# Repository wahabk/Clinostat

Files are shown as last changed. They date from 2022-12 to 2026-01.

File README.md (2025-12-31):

# OpenClino - Open-source 3D clinostat

Open-source 3D clinostat. A clinostat is a small scale [microgravity simulator](https://en.wikipedia.org/wiki/Random_positioning_machine).

Clinostat cad! cadModel
Clinostat real! realBuilt

This is based on the European Space Agency's work, specifically on [Jack Van Loon's clinorotation work](https://doi.org/10.3389/fpls.2019.01577).

OpenClino is designed to be simple, accessible, affordable, and **reliable**. It is designed to make use of 3D printing's strengths and requires *no machining* and minimum tools. To build OpenClino all non-printed parts are available off the shelf, mainly 3d printer stepper motors, belts, controllers, and skateboard bearings. All these parts are rated for thousands of hours of operation, and I have fully tested OpenClino to run for a minimum of 100 hours.

## Documentation

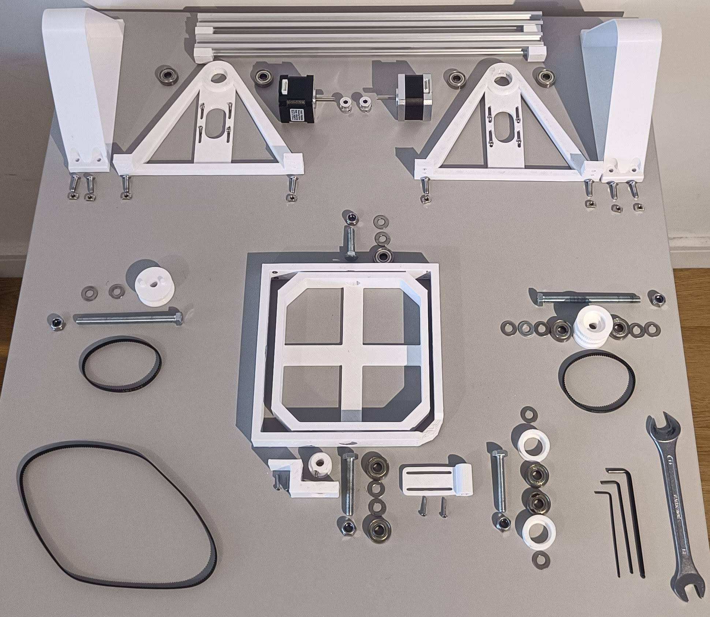
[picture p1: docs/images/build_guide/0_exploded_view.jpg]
Clinostat build!


I have provided:

- Docs in [`docs/1_documentation.md/`](docs/1_documentation.md) including circuit diagram.
- Code in [`src/`](src/openclino.ino)
- Code documentation in [`docs/4_code_documentation.md/`](docs/4_code_documentation.md/)
- 3D print files as .3MF in [`3d_files/`](3d_files/)
- Bill of materials in [`docs/2_BOM.md/`](docs/2_BOM.md/)
- Build guide in [`docs/3_build_guide.md/`](docs/3_build_guide.md/)

## Quick Usage

To run in clinorotation mode simply add these to your arduino's loop function, this will run the x axis at 3 rpm and the y axis at 4:

```cpp
void loop() {
    spin_continuous(3,4);
}
```

Don't forget to set the output pins for you motor controllers!

## Partial Gravity Simulation

Partial gravity simulations are now possible since Version 0.5.0. Instructions available in [`docs/1_documentation.md/`](docs/1_documentation.md).

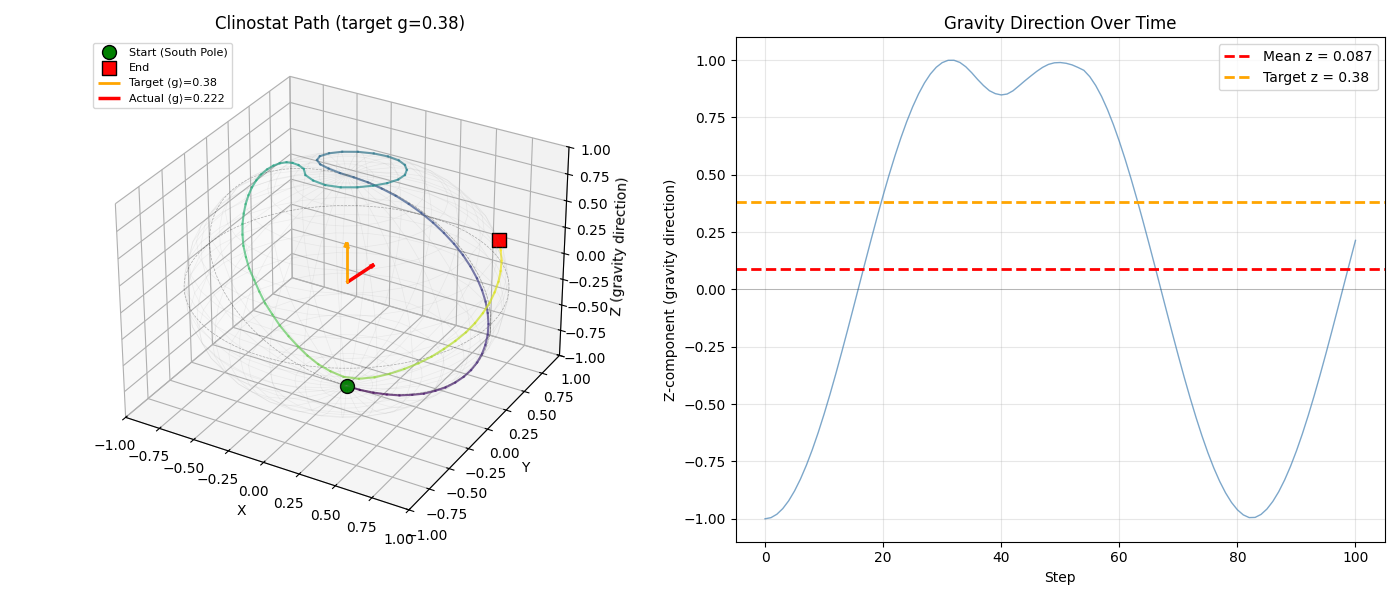
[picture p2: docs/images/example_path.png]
Partial gravity simulation.


## Contributors

[Dan Dragomirescu @dragomda](https://github.com/dragomda)

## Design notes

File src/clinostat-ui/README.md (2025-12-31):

# OpenClino UI

This directory contains scripts to run OpenClino with an LVGL screen connected to your Arduino.

Author: Dan Dragomirescu @dragomda

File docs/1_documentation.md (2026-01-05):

# OpenClino

It is very difficult to access a 3D clinostat, there are some companies that sell it but can be prohibitively expensive for gravity research. OpenClino can be built for £100 using off the shelf parts. OpenClino can run in continuous clinorotation or as a Random Positioning Machine (RPM).

> [!NOTE]  
> Since Version 0.3.0 remember to run the [calibration procedure](#usage--calibration).

## Definitions

- X body is the outer body. 
- Y body is the inner body.
- Motor pulleys attach to the motor.
- X/Y pulleys attach to the body.
- The "`m2y`" pulley is the one with 2 belts attached.
- The "`y_turn`" is the bearings bending the long y belt.
- The "`y_guide`" is the L shaped bracket holding the y pulley.

## Circuit design

This is a very simple arduino circuit with a button and 2 stepper motor controllers.

I base the circuit on [this great article by lastminuteengineers](https://lastminuteengineers.com/a4988-stepper-motor-driver-arduino-tutorial/]).

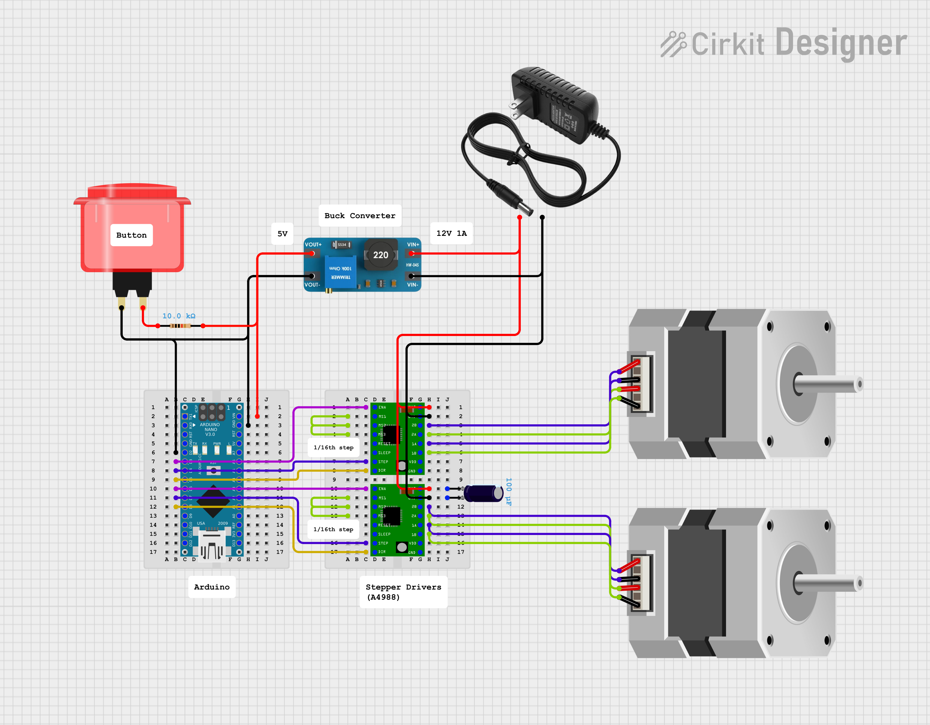
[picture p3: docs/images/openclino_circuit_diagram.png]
Clinostat circuit. Circuit diagram. Made with Cirkit Designer.


### Optional: MicroSD card reader

You can optionally add a MicroSD card reader to the circuit

Again I base the circuit on [this great article by lastminuteengineers](https://lastminuteengineers.com/arduino-micro-sd-card-module-tutorial/]).

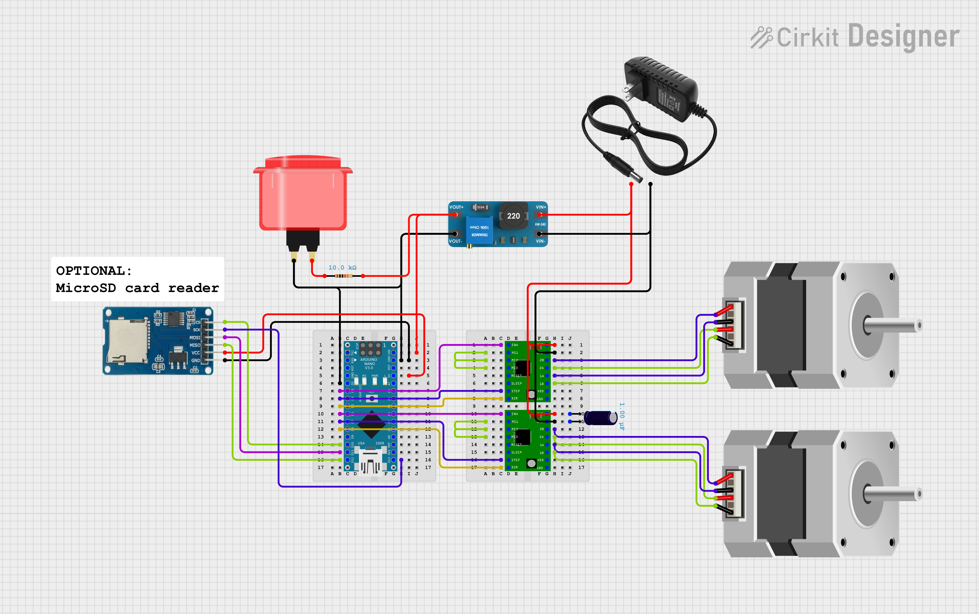
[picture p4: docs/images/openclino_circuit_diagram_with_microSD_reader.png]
Clinostat with MicroSD circuit. Circuit w/ SD diagram. Made with Cirkit Designer.


## Code

[OpenClino Documentation.](4_code_documentation.md)

## Usage
### Calibration

To calibrate the Y-axis correction factor, follow these steps:

1. Upload the code to your Arduino.
2. Open the Serial Monitor in the Arduino IDE.
3. Center the frames so that they are overlapping.
4. Press the button connected to the Arduino to start the calibration process.
5. The Y-axis motor will rotate by 360 degrees.
6. The Serial Monitor will prompt you to enter the actual degrees the Y-axis rotated.
7. Enter the measured degrees in the Serial Monitor and press Enter.
8. The new Y-axis correction factor will be calculated and displayed in the Serial Monitor.
9. Manually update the `yCorrection` variable in the code with the new correction factor.

Example:

```cpp
double yCorrection = 1.5; // Update this value with the new correction factor
```

> [!NOTE]  
> You might have to run the calibration a couple of times to get the right correction. The effect of the outer body on the inner body is dependant on friction in the system which is widely variable.

Now your clinostat is ready to use! To run in clinorotation mode simply add these to your arduino's loop function, this will run the x axis at 2 RPM and the y axis at 4:

```cpp
void loop() {
    spin_continuous(2,4);
}
```

### Partial gravity simulation

The scripts for partial gravity path generation can be found in `src/openclino/partial_gravity/`.

Partial gravity simulations require a more complex path to follow, which the arduino is not able to compute at runtime, therefore, this requires generating a path on your computer using a python script and reading the path on the arduino using a MicroSD card reader.

The method is based on a geodesic random walk on a spheroid. The sphere is sampled evenly which usually results in close to 0g, and the error from the target Gz is computed. A drift term is added to the clinostat's path to bias the running average Gz to converge to the target G. This is based on the paper - [Novel, Moon and Mars, partial gravity simulation paradigms and their effects on the balance between cell growth and cell proliferation during early plant development](https://www.ncbi.nlm.nih.gov/pmc/articles/PMC5884789/).

After setting up your arduino with a MicroSD card reader as shown in the Circuit Design documentation above, follow these steps:

1. Generate a path with `python generate_random_walk_path.py`
2. Visualise the path and average Gz with the above script until you are happy with the path. You may need to adjust `n_steps`, `step_size`, and the `control_window`.
3. Copy the generated `path.txt` to a MicroSD card and insert into the arduino reader.
4. Run `openclino.ino` with `follow_path();` uncommented. The serial Monitor will help debug any issues with the SD card.

### SD Card debugging

There can be faults with the MicroSD card reader, the card itself, or the file added.

1. Make sure the file is called `path.txt` or `PATH_FILENAME` is adjusted in `openclino.cpp`.
2. Make sure the file is in the root directory of the SD card (not inside another folder).
3. Use the debugging scripts to test the SD card and path file separately. Open your Serial Monitor and follow the instructions:
   1. Ensure the SD card and reader work with `test_sd/test_sd.ino`. This will read the SD card, write some text to the file `test.txt` and then read the file.
   2. Test that the path file works with `test_path/test_path.ino`. This will read each file line by line and verify it's format.

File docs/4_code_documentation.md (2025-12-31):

# OpenClino Documentation

This document provides reference information about the functions used to control stepper motors in the Arduino project. Each function is described with its purpose, parameters, and behavior. The documentation is generated using AI.

## Functions

### `void enable(bool enableX, bool enableY)`

Enables or disables the X and Y motors.

- **Parameters:**
  - `enableX` (bool): If `true`, enables the X-axis motor; if `false`, disables it.
  - `enableY` (bool): If `true`, enables the Y-axis motor; if `false`, disables it.

---

### `void spin_degs(float Q1_target, float Q2_target, float maxRPM = 10, int finalDelay = 100)`

Spins the X and Y motors by specified degrees at specified speeds.

- **Parameters:**
  - `Q1_target` (float): Degrees to rotate the X-axis motor.
  - `Q2_target` (float): Degrees to rotate the Y-axis motor.
  - `maxRPM` (float, default = 10): Maximum speed of the motors in RPM.
  - `finalDelay` (int, default = 100): Delay in milliseconds after stopping the motors.

---

### `void spin_continuous(float speedX = 10, float speedY = 10, int buttonDelay = 1000)`

Spins the X and Y motors continuously at specified speeds until a button is pressed.

- **Parameters:**
  - `speedX` (float, default = 10): Speed of the X-axis motor in RPM.
  - `speedY` (float, default = 10): Speed of the Y-axis motor in RPM.
  - `buttonDelay` (int, default = 1000): Delay in milliseconds after stopping the motors.

---

### `void calibrate_y_correction()`

Calibrates the Y-axis correction factor by rotating the Y-axis motor and measuring the actual rotation.

---

## Tests

### `void test_pulley_ratios()`

Tests the pulley ratios by rotating the X and Y motors by 360 degrees and back.

---

### `void test_spin_degs_multi()`

Tests the `spin_degs` function with multiple rotations.

---

### `void follow_path()`

Reads `PATH_FILENAME` (by default `path.txt`) from an SD card, and executes `spin_degs()` on each line of the file. The function will error if the SD card can't be read or if the file is not found.

---

### `void setup()`

Initializes the Arduino pins and serial communication, and prints a welcome message.

---

### `void loop()`

Main loop that reads the button state and performs actions based on the button press.

- **Behavior:**
  - Turns off motors when the button is not pressed.
  - When the button is pressed, it turns on the motors, lights up the built-in LED, and runs calibration and test functions.

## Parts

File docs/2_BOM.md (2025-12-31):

# Bill of Materials

#### To Buy

| Category     | Quantity | Description                                 | Specifications              |
|--------------|----------|---------------------------------------------|-----------------------------|
| Electronics  | 1        | Arduino (your choice)                       | -                           |
|              | 2        | Nema 17 motors                              | 0.42Nm                      |
|              | 2        | Stepper motor controllers                   | A4988 drivers are cheap. TMC2208 drivers will give better, silent operation with less vibration.                       |
|              | 1        | Power supply                                | -                           |
|              | 1        | MicroSD card reader                         | Optional, required for partial gravity. 5V 6 spin SPI interface SD card reader |
| Hardware     | 2        | GT2 belts                                   | 200mm, 6mm width            |
|              | 1        | GT2 belt                                    | 500mm, 6mm width            |
|              | 2        | Stepper motor timing pulleys                | 16 tooth                    |
|              | 1        | GT-2 Pulley (y_pulley)                      | 30 tooth, 8mm bore, 6mm width |
|              | 1        | Aluminium extrusion                         | 1mx20mmx20mm (cut in half)  |
|              | 12       | Skateboard bearings                         | 8mm (ID), 22mm (OD)         |
| Bolts        | 4        | Hex bolts                                   | M8 by 60mm                  |
|              | 2        | Hex bolts                                   | M8 by 100mm                 |
|              | 8        | Alan bolts                                  | M3 by 12mm                  |
|              | 12       | Alan bolts                                  | M5 by 16mm                  |
|              | 13       | Washers                                     | M8 (8mm ID, 16mm OD)        |
| Miscellaneous| 1        | Printing filament                           | 1KG, your choice of filament|

#### To Print

| Quantity | Description    | Note              |
|----------|----------------|-------------------|
| 2        | m_enclosure    | -                 |
| 2        | m_mounts       | -                 |
| 1        | x_body         | -                 |
| 1        | x_pulley       | -                 |
| 1        | y_body         | -                 |
| 1        | m2y_pulley     | Needs Supports    |
| 1        | y_turn         | -                 |
| 2        | y_turn_pulley  | -                 |
| 1        | y_guide        | -                 |

All files are available in `3d_files/`.

All the parts are printed with 20% infill, and I use an Ender 3 printer. I usually have to sand down the edges due to stringing etc.
According to your printer's over/under extrusion you might have to sand down edges, or add silicon tape to the bolt heads so they key into the bodies.
I personally prefer to use a brim.

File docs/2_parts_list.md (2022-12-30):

# Parts list

## To buy

- 2 x nema 17 motors
- 2 x stepper motor controllers (A4988)
- 2 x 180mm GT2 belts
- 1 x 220mm GT2 belt
- 2 x stepper motor pulleys
- 1m 20x20 aluminium extrusion
- 12 x 8mm skateboard bearings

Hardware
- 4 x m8 by 60mm hex bolts
- 2 x m8 by 100mm hex bolts
- 8 x m3 bolts
- 12 x m5 by 

- 1KG of your printing filament of choice

## To print

- 2 x m_enclosure
- 2 x m_mounts
- x_body
- x_pulley
- y_body
- m2y_pulley
- y_turn
- 2 x y_turn_pulley
- y_guide
- y_pulley

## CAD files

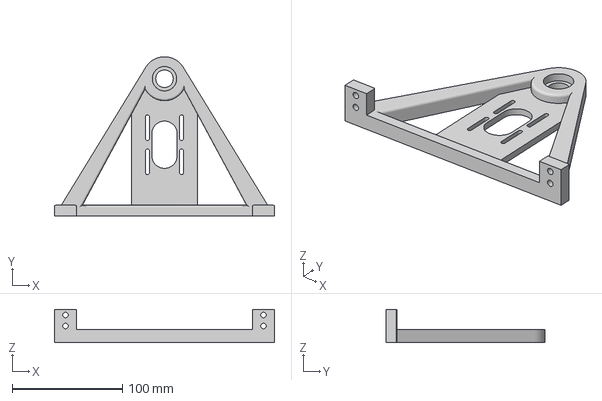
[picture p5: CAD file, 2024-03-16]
3d_files/m_base v9.3mf
200.0 x 145.0 x 30.0 mm

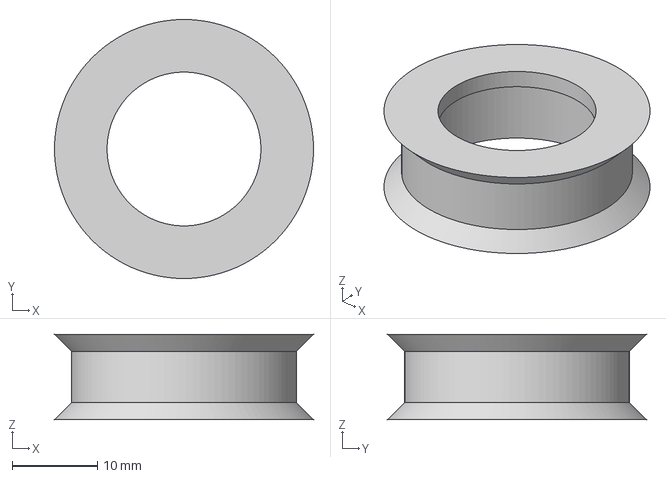
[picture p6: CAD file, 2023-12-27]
3d_files/y_turn_pulley v2.3mf
30.3 x 30.3 x 10.0 mm

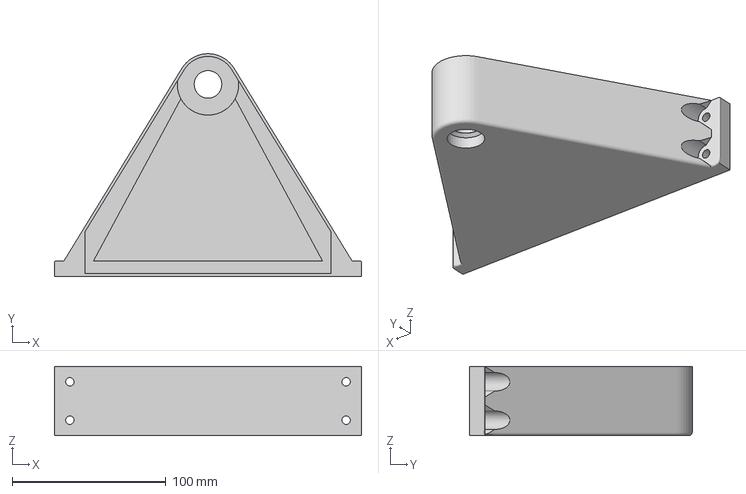
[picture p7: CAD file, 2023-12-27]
3d_files/m_enclosure v2.3mf
200.0 x 145.0 x 45.0 mm

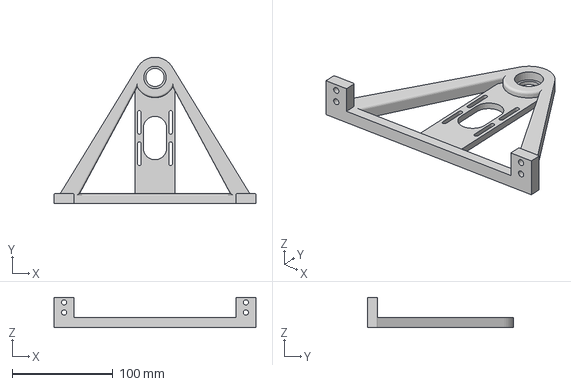
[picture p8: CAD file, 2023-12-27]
3d_files/m_base v7.3mf
200.0 x 145.0 x 30.0 mm

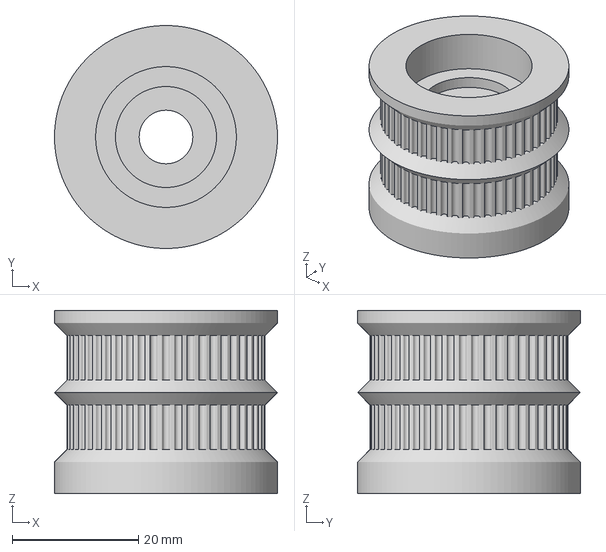
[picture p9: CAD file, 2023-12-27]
3d_files/m2y v5.3mf
35.3 x 35.3 x 29.0 mm

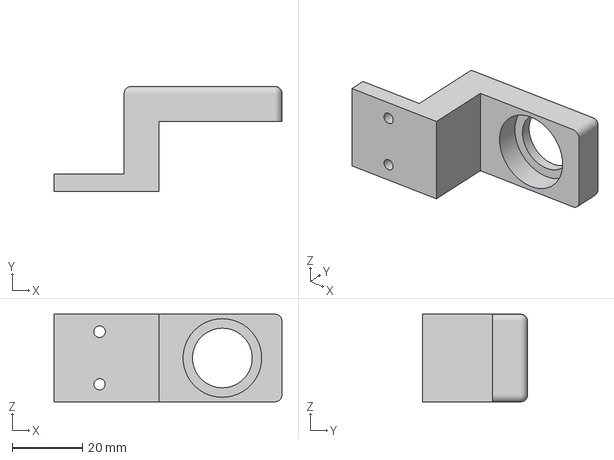
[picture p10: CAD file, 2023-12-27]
3d_files/y_guide v2.3mf
65.0 x 30.0 x 25.0 mm

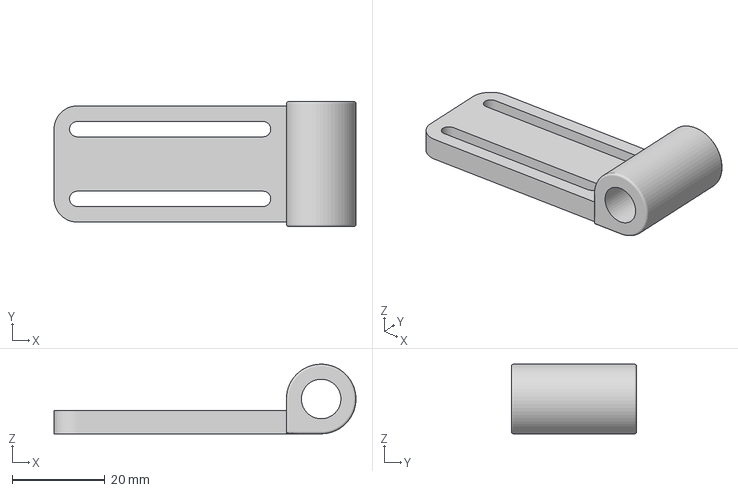
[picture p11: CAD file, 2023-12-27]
3d_files/y_turn v2.3mf
65.0 x 27.0 x 15.0 mm

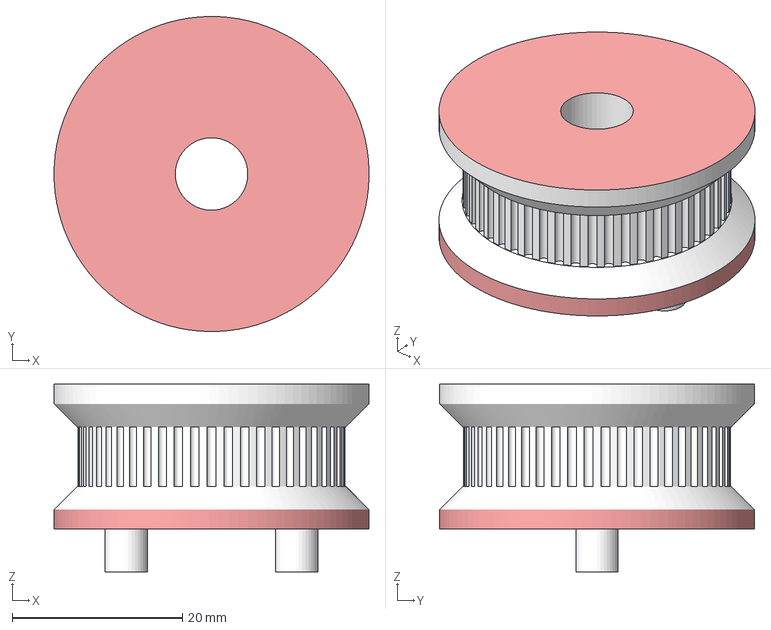
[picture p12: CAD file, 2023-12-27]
3d_files/x_pulley v7.3mf
37.0 x 37.0 x 22.0 mm

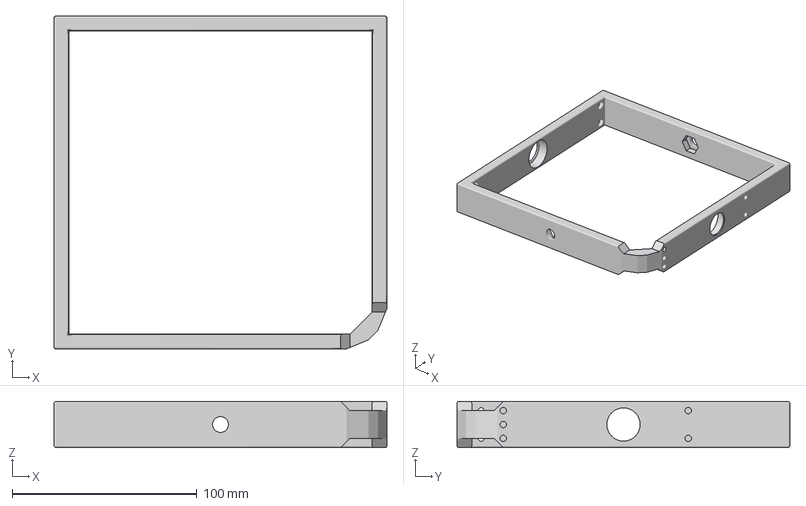
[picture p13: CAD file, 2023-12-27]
3d_files/x_body v9.3mf
180.0 x 180.0 x 25.0 mm

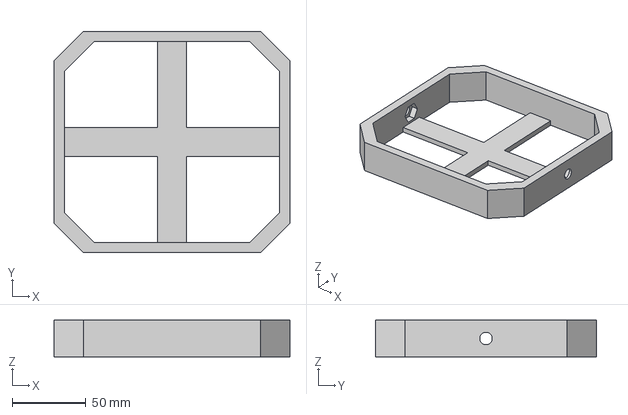
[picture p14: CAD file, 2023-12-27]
3d_files/y_body v4.3mf
160.0 x 150.0 x 25.0 mm

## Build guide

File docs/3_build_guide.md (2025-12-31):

# OpenClino Build Guide
y_turn

## Contents

- [OpenClino Build Guide](#openclino-build-guide)
  - [Contents](#contents)
  - [3D Printing](#3d-printing)
  - [Hardware](#hardware)
    - [Tools required:](#tools-required)
  - [Build Instructions:](#build-instructions)
    - [**1 - Build y\_turn.**](#1---build-y_turn)
    - [**2 - Combining x and y bodies.**](#2---combining-x-and-y-bodies)
    - [**3 - x\_pulley and m2y pulley.**](#3---x_pulley-and-m2y-pulley)
    - [**4 - Build the base.**](#4---build-the-base)
    - [**5 - Final Assembly.**](#5---final-assembly)

## 3D Printing

All files are available in `3d_files/`.
The parts can be printed in PLA but I prefer to use PETG. 

## Hardware

The build of openclino usually takes 1-2 hours. Step 0 is make sure you make a coffee or your favourite hot/cold beverage.
We will build the sub assemblies: y_turn, bodies, and the base, and the final step 5 is to combine everything.

### Tools required:

- Spanner/wrench: Number 13 metric (same as a skateboard).
- Alan keys: 3 mm for the base.
            2 mm for the motors and bodies.
            1.5 mm for the motor pulley grub screw.

## Build Instructions:

Ensure you have all the parts from the [Bill of Materials](2_BOM.md).

### **1 - Build y_turn.**

a) Place the washers between the bolthead/nut and the bearing.

>[!NOTE]
> Don't tighten the nuts too much as this will introduce a lot of unwanted friction.

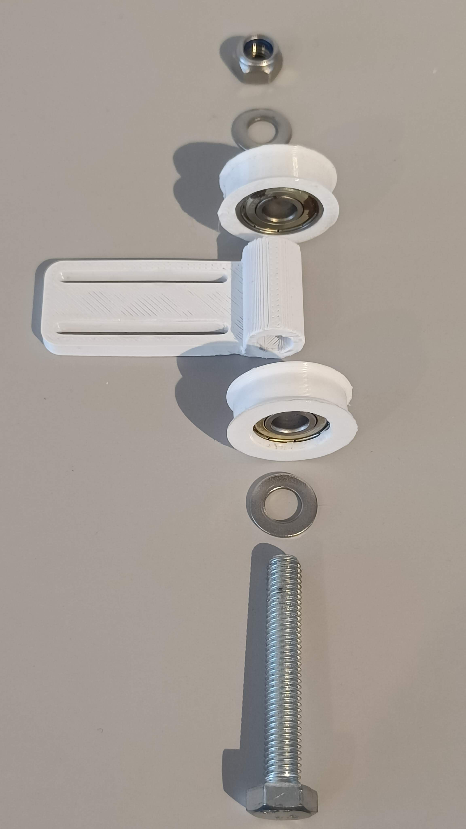
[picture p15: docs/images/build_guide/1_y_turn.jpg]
y_turn


### **2 - Combining x and y bodies.**

a) Push fit bearings to the y_guide and the x body. 

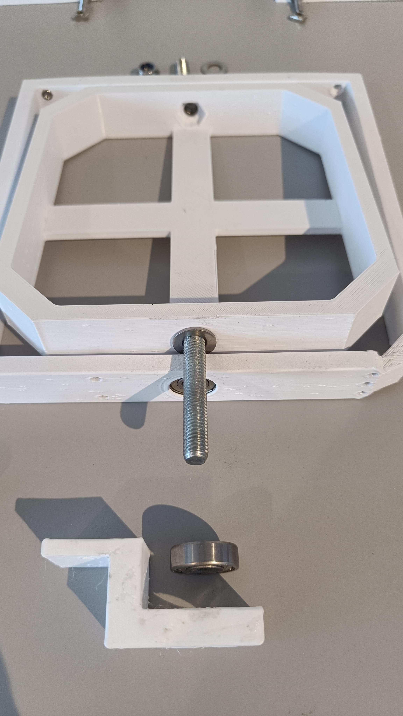
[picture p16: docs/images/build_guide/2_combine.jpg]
combine


b) Install bolts through the x and y body, make sure to put a washer on each side of the bearing.

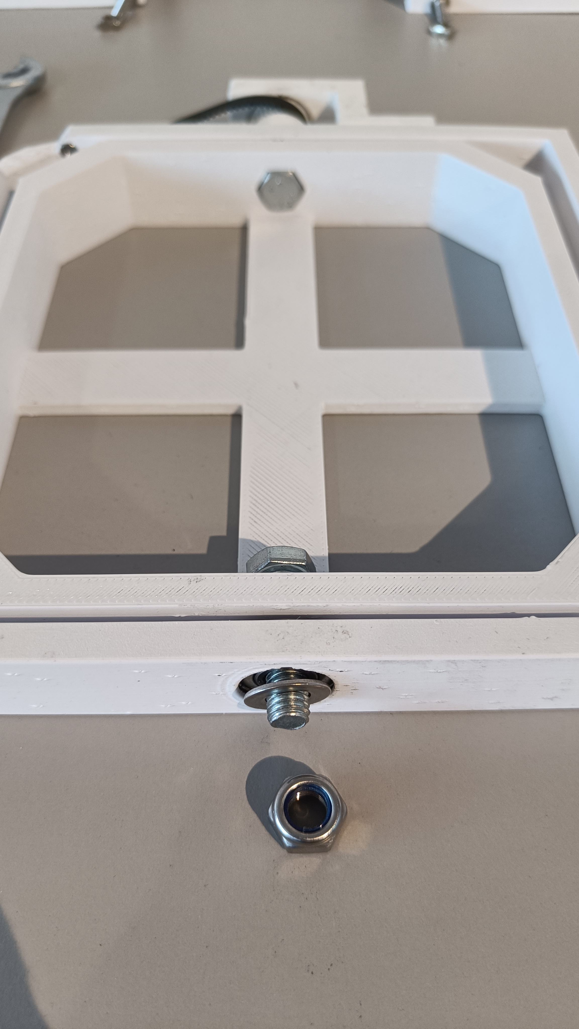
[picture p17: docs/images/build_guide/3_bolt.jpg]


c) Install y_pulley and y_guide, with washers in between. 
   
>[!NOTE]
> Remember to add the y belt before the nut!

The hex nuts can be push fit into the x body.

Tighten the y_pulley grub screw(s) so that it rotates with the y body.

>[!NOTE]
> The y_pulley has been updated since version 0.4 to be an off the shelf 6mm GT2 30T pulley, instead of a 3D printed part as shown in these pictures.

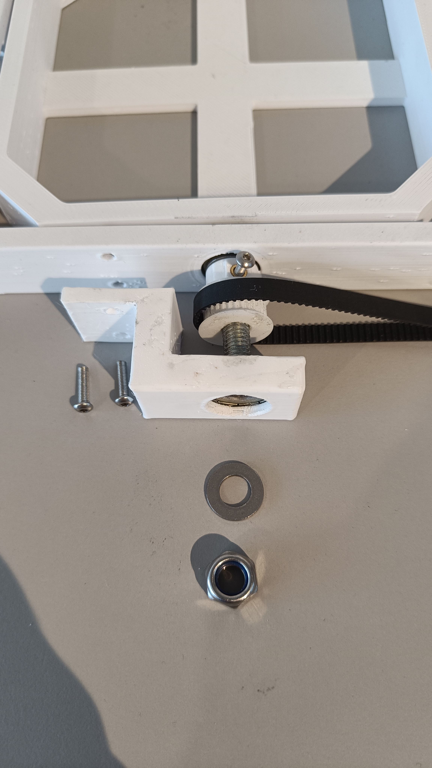
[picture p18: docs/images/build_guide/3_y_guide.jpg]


d) Install the y_turn into the x body. The hex nuts can be push fit into the x body.

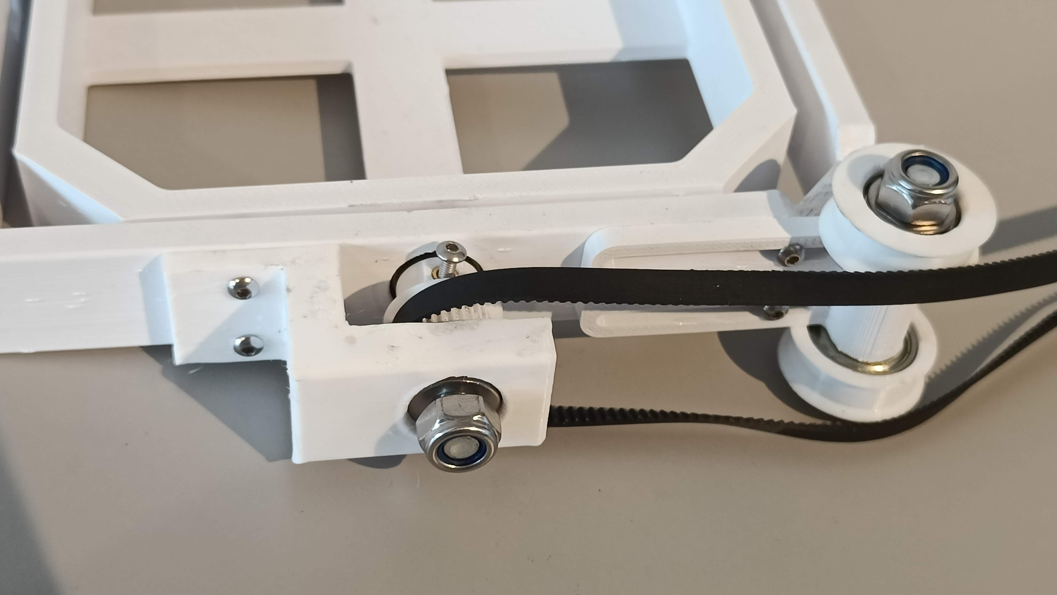
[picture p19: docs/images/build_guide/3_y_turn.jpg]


e) Ensure everything rotates smoothly. The Nylock nuts don't have to be tightened, just enough so that it doesn't shake.

### **3 - x_pulley and m2y pulley.**

Now that x and y are combined, lets add the x_pulley and m2y pulley.

a) x_pulley: push fit the x pulley into the body, and place washers in for now. You might have to sand the pins on the x_pulley.

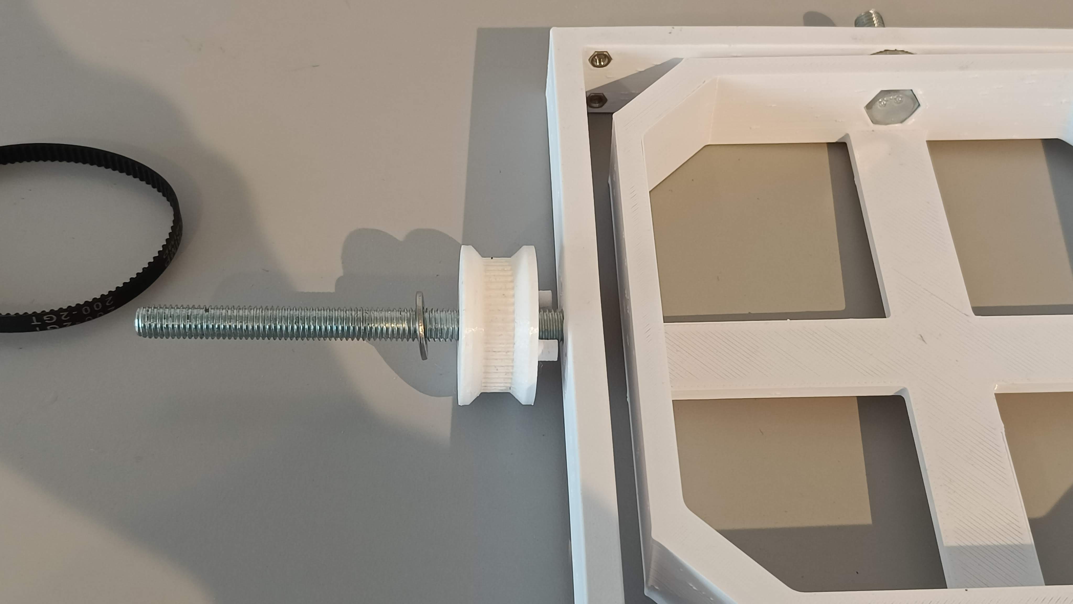
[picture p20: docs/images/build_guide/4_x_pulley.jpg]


b) m2y pulley: push fit two bearings into the m2y pulley and add washers for now.
   
>[!NOTE]
> The tricky part here is making sure the long belt doesnt scrape the motor like step 5e, so remember to keep the wider part of the m2y close to the x body, and place 2 or 3washers between the x body and the m2y pulley.

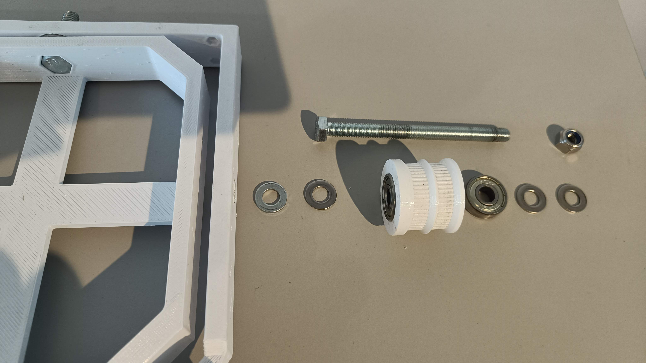
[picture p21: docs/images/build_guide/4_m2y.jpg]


We have now fully combined x and y bodies!

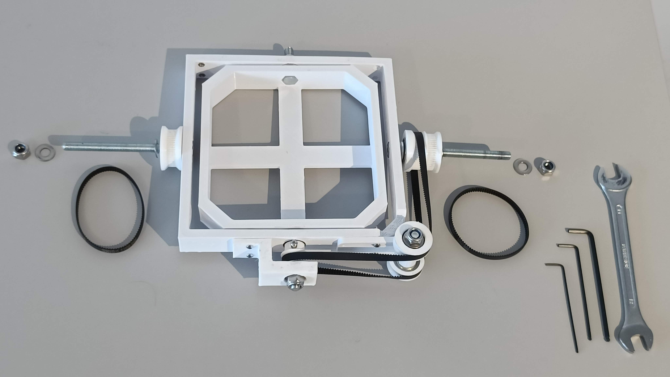
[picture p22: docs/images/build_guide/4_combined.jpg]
combine

 
### **4 - Build the base.**

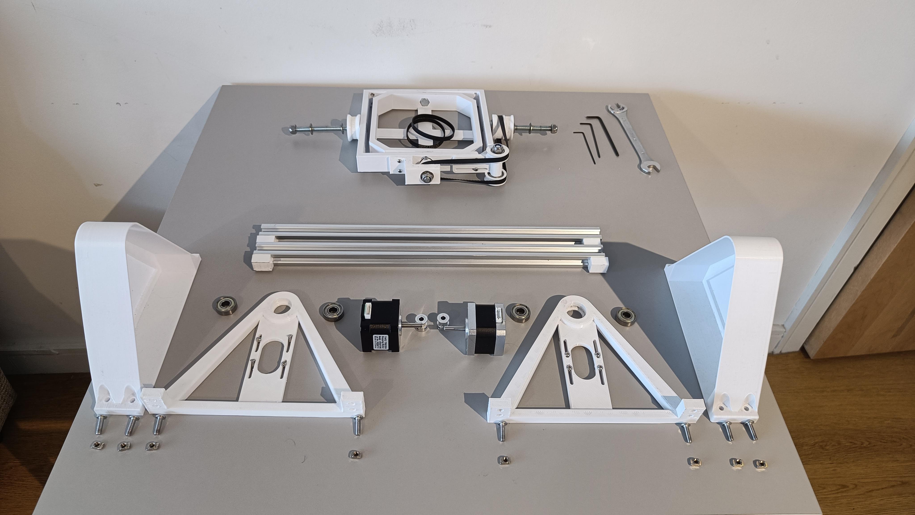
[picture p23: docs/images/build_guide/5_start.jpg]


a) Install the motor pulleys.
   
Make sure to align the notch in the motor shaft with one of the grub screws in the pulley.

Keep the motors loose for now as you will need to tension the belts later.

Repeat for both sides.

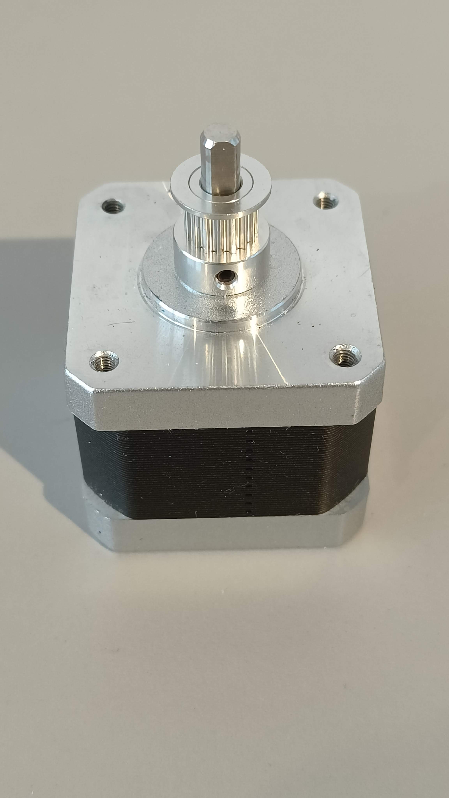
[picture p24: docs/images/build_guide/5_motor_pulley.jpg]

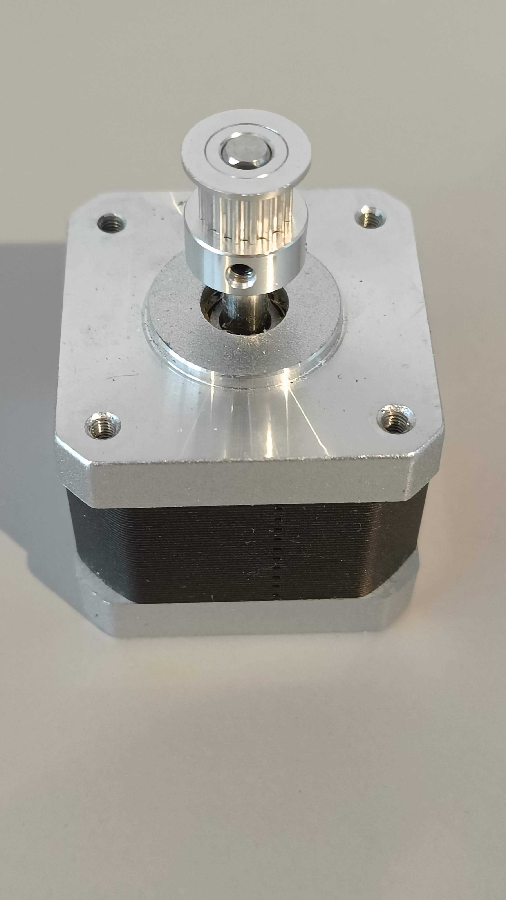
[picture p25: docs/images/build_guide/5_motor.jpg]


b) Install the motor to the motor mount using 4 hex screws.

You can also push fit the bearings into the motor mount.

Repeat for both sides.

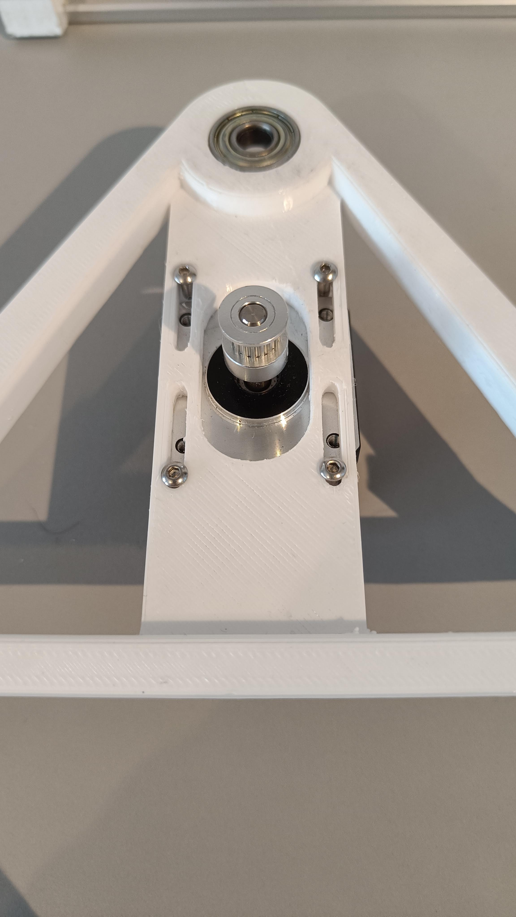
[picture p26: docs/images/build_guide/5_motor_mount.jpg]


c) Push fit the bearings into the motor_mount and motor_enclosure.

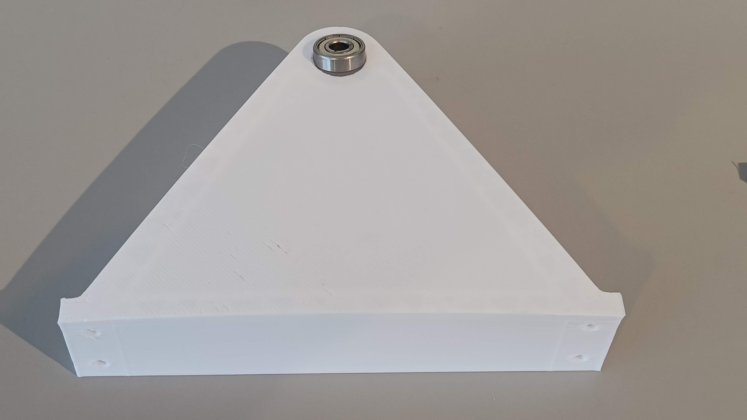
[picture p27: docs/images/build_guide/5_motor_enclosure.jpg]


d) Install the enclosures and motor mounts to the aluminium rails.
   
Keep all the screws loose for now, it will take a lot of wiggling to align everything!

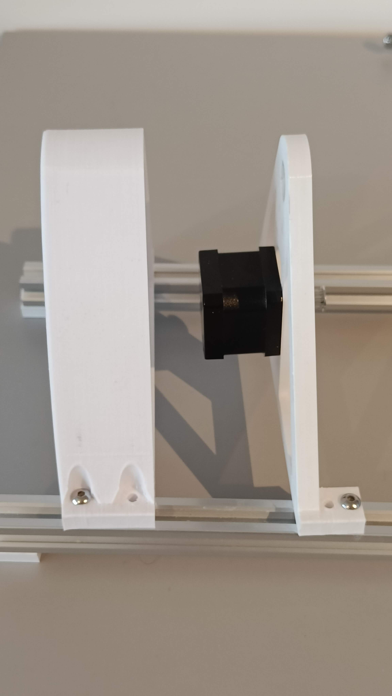
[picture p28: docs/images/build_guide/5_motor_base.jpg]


### **5 - Final Assembly.**

You should now have two assemblies; the base, and the x+y bodies.

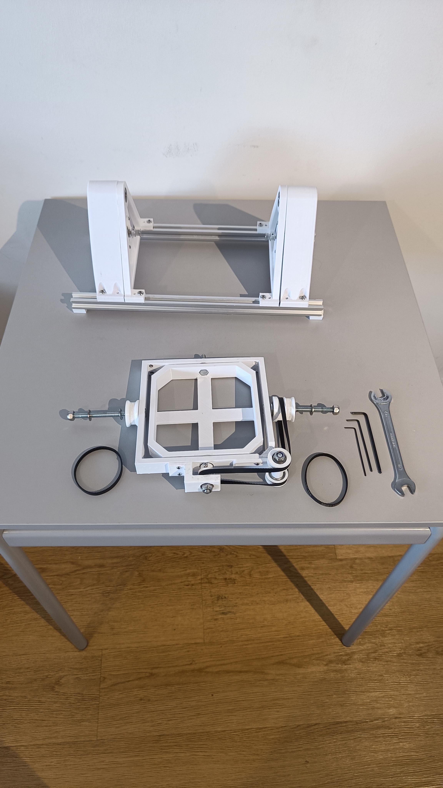
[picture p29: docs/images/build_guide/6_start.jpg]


a) Add the short belts to the x_pulley and m2y_pulley.

b) Mount the x_body assembly to the base.
   
Remember to add a washer between the pulleys and the motor_mount bearings.

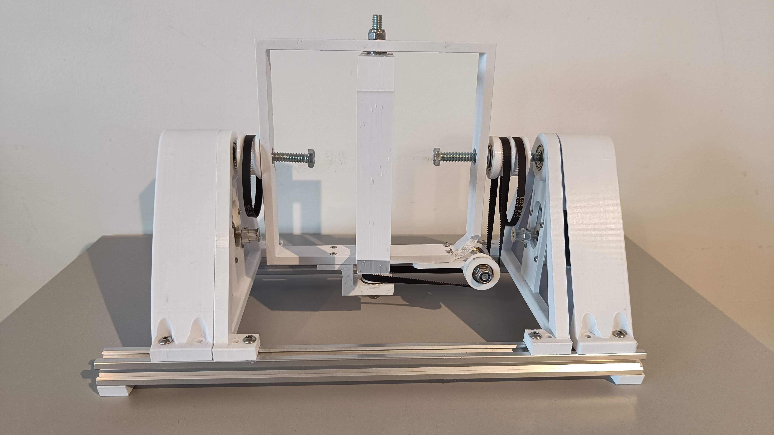
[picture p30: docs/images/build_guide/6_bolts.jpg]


c) Tighten the long bolts but not too much, as it might break the mounts and enclosures.
   
Again you don't want anything to be tight, make sure it all spins smoothly.

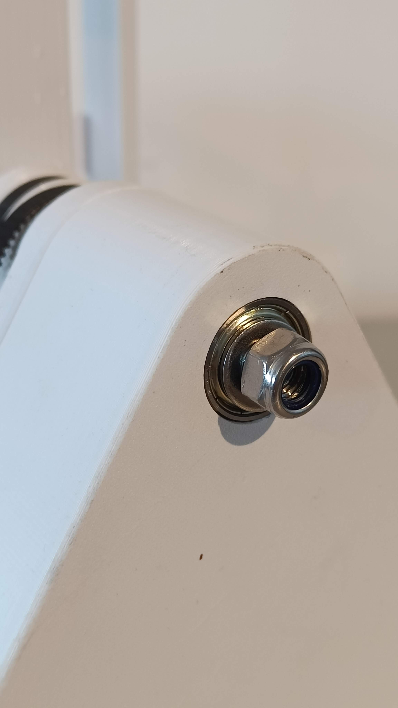
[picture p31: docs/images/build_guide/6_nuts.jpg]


d) Hook the short belts to the motor pulley.
   
You will have to lift the motors up to attach the belt, then tension the belt and tighten the motor screws.

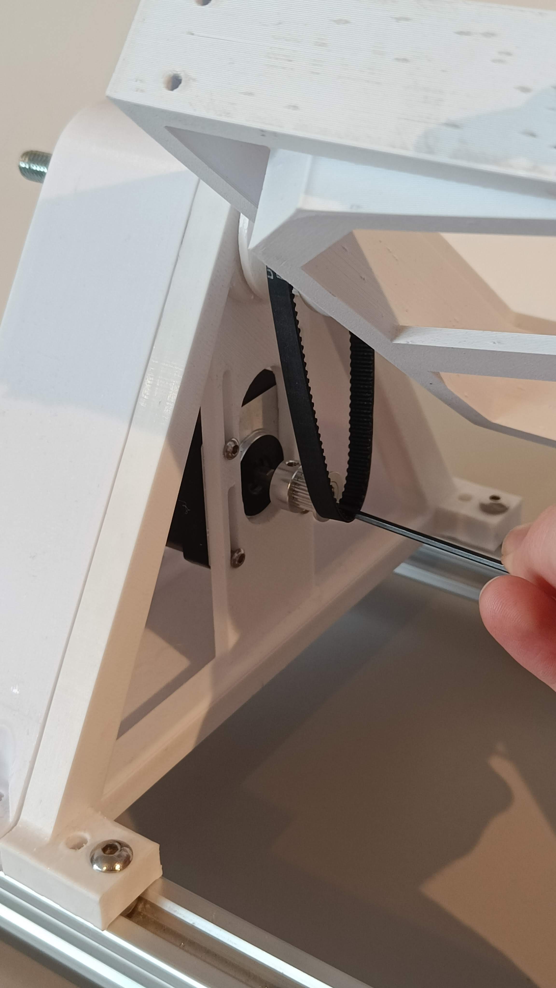
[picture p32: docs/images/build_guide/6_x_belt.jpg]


e) This step is just to ensure that the y belt (short) m2y belt (long) don't interfere.
   
This is the tightest tolerance in the clinostat.

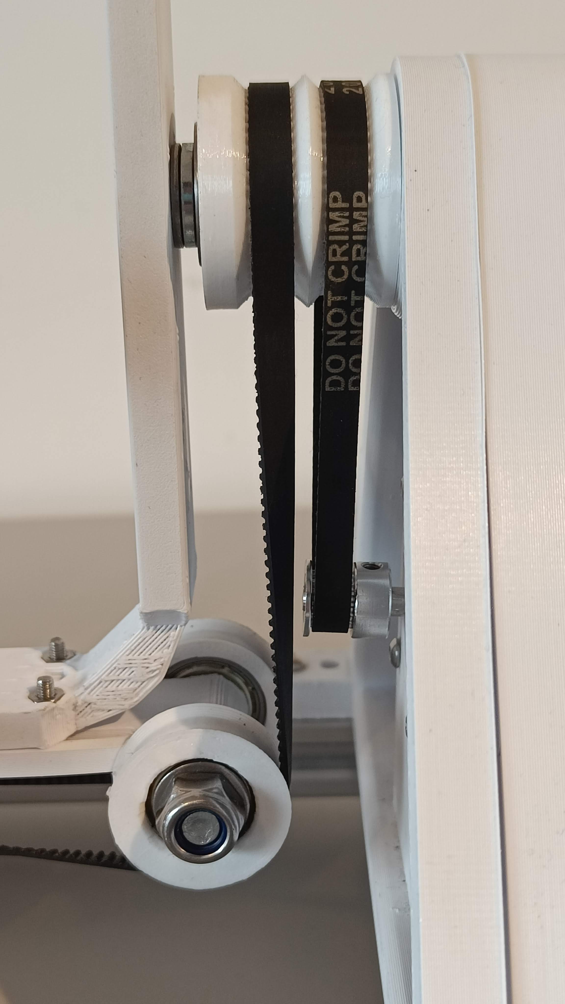
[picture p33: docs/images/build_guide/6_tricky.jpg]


f) Finally, only after installing everything and ensuring both axes rotate smoothly should you tighten the base.

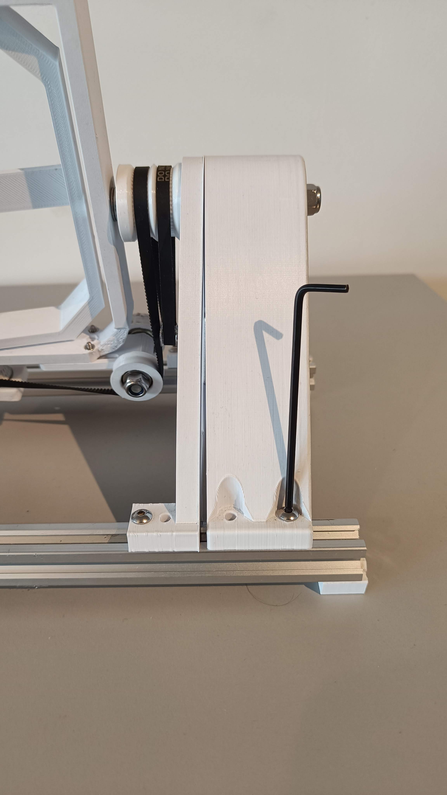
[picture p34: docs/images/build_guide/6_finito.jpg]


Make sure every pulley and axis rotates smoothly. If there is friction anywhere you might have to loosen the bolts or sand down interference from your prints.

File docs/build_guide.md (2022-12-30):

# OpenClino Build Guide

## 3D Printing

The parts can be printed in PLA but I prefer to use PETG.

All the parts are printed on an ender 3.

## Electronics

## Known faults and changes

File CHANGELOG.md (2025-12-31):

# Version 0.5.0 31/12/2025

## Major Partial Gravity Simulation Update

- Restructure to modular code `openclino.h` (header file), `openclino.cpp` (code), and `openclino.ino` (arduino).
- MicroSD card.
  - Add MicroSD card reader to optional circuit design image.
  - Add MicroSD card debugging scripts `test_sd` and `test_path`.
- Partial gravity.
  - Add `void follow_path()` to `openclino.cpp`
  - Add `src/openclino/partial_gravity/` scripts `generate_test_path.py` and `generate_random_walk_path.py`
- Respective documentation updates for all above.
- Remove vestigial `src/raspberry_pi` IMU code.
- Add `.gitignore`.

# Version 0.4.0 26/12/2025

This update mainly replaces the 3D printed y_pulley with an off the shelf 30 tooth GT2 pulley.

- y_pulley.3mf removed.
- Build guide updated and admonition removed.
- BOM updated respectively to move y_pulley from printed to bought parts.

# Version 0.3.2 02/06/2025

- Fix `calibrate_y_correction()`:
  - Check for `0.0` for `calibrate_y_correction()`.
- General comment additions.

# Version 0.3.1 15/03/2025

- Check for `NULL` input in `calibrate_y_correction()`.

# Version 0.3.0 22/02/2025

- Major refactor to functions `spin_degs()` and `spin_continuous()` now precompute compensation instead of relying on if statements.
- `calibrate_y_correction()` added to measure `yCorrection` using user input.
- `clockwise` functions removed for direction pin handling.
- `RPM()` removed for now.
- General docs updates.

# Version 0.2.2 09/02/2025

- Add `diagnose_rotation_error()` to measure `yCorrection`.
- Restructure to include `openclino.ino` into the folder `openclino/` so arduino IDE.
- Remove epsilon to `double yCorrection`.
- update `interval` to double and `currentTime` measurements.

# Version 0.2.1 01/12/2024

- Fix `spin_continuous()` to not use `AccelStepper` and to compensate motors for each other.
- Reset `epsilon` to 1.

# Version 0.2.0 29/11/2024

- Changed pulley diameters to pulley teeth
- Added `float epsilon` for calibrating substeps.
- Added circuit diagram.
- Updated documentation and README.md
- updated `spin_degs()` if statements and compensation.
- Added unit tests `calibrate_pulley_teeth()` and `test_spin_degs_multi()`.

# Version 0.1.0 22/11/2024

Initial release. Development till 22/11/2024.

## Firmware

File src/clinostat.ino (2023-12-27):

// Define steps per revolution
const int motorSteps = 200;
const int subStep = 16;
const unsigned long stepsPerRevolution = motorSteps * subStep;

//pins
const int buttonPin = 2;
const int enablePinX = 3;
const int stepPinX = 4;
const int dirPinX = 5;
const int enablePinY = 6;
const int stepPinY = 7;
const int dirPinY = 8;

// pulley diameters
// try n teeth
const float xMotD = 9.5;
const float xPulleyD = 31.5;
const float yMotD = 9.5;
const float yTurnD = 31.5;
const float yPulleyD = 18.5;
const double xRatio = xMotD / xPulleyD; // diameters
const double yRatio = yMotD / yPulleyD;
const int nStepsXperRot = stepsPerRevolution / xRatio;
const int nStepsYperRot = stepsPerRevolution / yRatio;

int buttonState = 0;

void wake(bool x, bool y) {
  if (x == true) {digitalWrite(enablePinX, LOW);}
  else           {digitalWrite(enablePinX, HIGH);}
  if (y == true) {digitalWrite(enablePinY, LOW);}
  else           {digitalWrite(enablePinY, HIGH);}
}

void xClockwise(bool foo) {
  if (foo == true) {digitalWrite(dirPinX, HIGH);}
  else             {digitalWrite(dirPinX, LOW);}
}

void yClockwise(bool foo) {
  if (foo == true) {digitalWrite(dirPinY, LOW);}
  else             {digitalWrite(dirPinY, HIGH);}
}

//function to continuous spin x and y given <run_time> and rpm where if 0 keep still
//function to spin <degX, degY> and <rpms>
//void spin_degs():
//think about smoothing

void spin_continuous(int t = 1, float speedX = 10, float speedY = 10, int finalDelay=100) {
  bool xClock;
  bool yClock;

  if (speedX >= 0) {xClock = true;}
  else           {xClock = false;}
  if (speedY >= 0) {yClock = true;}
  else           {yClock = false;}

  long IntervalX =  (6e7 / speedX) / nStepsXperRot;
  long IntervalY =  (6e7 / speedY) / nStepsYperRot;
  unsigned long stepsY = 0;
  unsigned long stepsX = 0;
  unsigned long previousTimeX = micros();
  unsigned long previousTimeY = micros();

  while (true) {
    unsigned long currentTimeX = micros();
    unsigned long currentTimeY = micros();
    bool xGo = false; // whether to step x
    bool yGo = false; // whether to step y
    bool skipCompensation = false; 
    
    digitalWrite(stepPinX, HIGH);
    digitalWrite(stepPinY, HIGH);
    
    if (currentTimeX - previousTimeX > IntervalX) {xGo = true;}
    if (currentTimeY - previousTimeY > IntervalY) {yGo = true;}
    if (yGo == true && xGo == true && yClock == false && xClock != yClock) {skipCompensation = true;}

    if (xGo) {
      xClockwise(xClock);
      digitalWrite(stepPinX, LOW);
      digitalWrite(stepPinX, HIGH);
      previousTimeX = currentTimeX;

      if (skipCompensation == false) {
        yClockwise(!xClock); // spin y motor with x
  
        digitalWrite(stepPinY, LOW); //compensator
        digitalWrite(stepPinY, HIGH);
      }
      stepsX++;
    }

    if (yGo) {
      yClockwise(yClock);
      digitalWrite(stepPinY, LOW);
      digitalWrite(stepPinY, HIGH);
      previousTimeY = currentTimeY;
      stepsY++;
    }
//    if (stepsX >= nStepsX && stepsY >= nStepsY) {keepGoing = false;} // check if finished
  }
  delay(finalDelay);
}

void spin_degs(float degX, float degY, float speedX = 60, float speedY = 60, int finalDelay = 100) {
//  wake(true, true);

  // define directions because y motor has to constantly change direction to compensate
  bool xClock;
  bool yClock;

  if (degX >= 0) {xClock = true;}
  else           {xClock = false;}
  if (degY >= 0) {yClock = true;}
  else           {yClock = false;}

  int nStepsX = nStepsXperRot * abs(degX / 360.); // define fraction of full turn
  int nStepsY = nStepsYperRot * abs(degY / 360.);

  bool keepGoing = true;

  long IntervalX =  (6e7 / speedX) / nStepsXperRot;
  long IntervalY =  (6e7 / speedY) / nStepsYperRot;
  unsigned long stepsY = 0;
  unsigned long stepsX = 0;
  unsigned long previousTimeX = micros();
  unsigned long previousTimeY = micros();
  
  while (keepGoing) {
    unsigned long currentTimeX = micros();
    unsigned long currentTimeY = micros();
    bool xGo = false; // whether to step x
    bool yGo = false; // whether to step y
    bool skipCompensation = false; 
    
    digitalWrite(stepPinX, HIGH);
    digitalWrite(stepPinY, HIGH);
    
    if (currentTimeX - previousTimeX > IntervalX && stepsX <= nStepsX) {xGo = true;}
    if (currentTimeY - previousTimeY > IntervalY && stepsY <= nStepsY) {yGo = true;}
    if (yGo == true && xGo == true && yClock == false && xClock != yClock) {skipCompensation = true;}

    if (xGo) {
      xClockwise(xClock);
      digitalWrite(stepPinX, LOW);
      digitalWrite(stepPinX, HIGH);
      previousTimeX = currentTimeX;

      if (skipCompensation == false) {
        yClockwise(!xClock); // spin y motor with x
  
        digitalWrite(stepPinY, LOW); //compensator
        digitalWrite(stepPinY, HIGH);
      }
      stepsX++;
    }

    if (yGo) {
      yClockwise(yClock);
      digitalWrite(stepPinY, LOW);
      digitalWrite(stepPinY, HIGH);
      previousTimeY = currentTimeY;
      stepsY++;
    }
    if (stepsX >= nStepsX && stepsY >= nStepsY) {keepGoing = false;} // check if finished
  }
  delay(finalDelay);
}

void show_off(){
  spin_degs(180, 180);
  spin_degs(-180, -180);
  spin_degs(-180, 180);
  spin_degs(180, -180);
}

void RPM(){
  spin_degs(random(-360,360), random(-360,360));
}

void setup() {
  // put your setup code here, to run once:
  pinMode(buttonPin, INPUT);
  pinMode(LED_BUILTIN, OUTPUT);
  pinMode(stepPinX, OUTPUT);
  pinMode(dirPinX, OUTPUT);
  pinMode(stepPinY, OUTPUT);
  pinMode(dirPinY, OUTPUT);
  pinMode(enablePinX, OUTPUT);
  pinMode(enablePinY, OUTPUT);
  Serial.begin(9600);
  Serial.print("--\nHello\n--");

  wake(false, false);
}

void loop() {
  buttonState = digitalRead(buttonPin);

  wake(false, false);

  if (buttonState == HIGH) {
    digitalWrite(LED_BUILTIN, HIGH);
    wake(true, true);
    spin_continuous(1,60,60);
  //    show_off();
  //    RPM();
  }

  digitalWrite(LED_BUILTIN, LOW);
  delay(10); // Wait a second
}

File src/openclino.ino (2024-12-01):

#include <AccelStepper.h>

// pins
const int buttonPin = 2;
const int enablePinX = 3;
const int stepPinX = 4;
const int dirPinX = 5;
const int enablePinY = 6;
const int stepPinY = 7;
const int dirPinY = 8;

// Define steps per revolution
const int motorSteps = 200;
const int subStep = 16;
const unsigned long stepsPerRevolution = motorSteps * subStep;
// eposilon to fix discrepancy between motor substeps
// set to 1 to undo calibration.
const double epsilon = 1;

// Pulley teeth
const float xMotTeeth = 16;
const float xPulleyTeeth = 50;
const float yMotTeeth = 16;
const float yTurnTeeth = 50;
const float yPulleyTeeth = 20;

// Calculate the gear ratios based on pulley teeth
const double xRatio = xPulleyTeeth / xMotTeeth;
const double yRatio1 = yTurnTeeth / yMotTeeth;
const double yRatio2 = yPulleyTeeth / yTurnTeeth;
const double yRatio = yRatio1 * yRatio2 * epsilon;

// Calculate effective steps per rotation
const double nStepsPerRotX = stepsPerRevolution * xRatio;
const double nStepsPerRotY = stepsPerRevolution * yRatio;

int buttonState = 0;

// Define AccelStepper objects for X and Y axes
AccelStepper stepperX(1, stepPinX, dirPinX);
AccelStepper stepperY(1, stepPinY, dirPinY);

void wake(bool x, bool y)
{
  if (x == true)
  {
    digitalWrite(enablePinX, LOW);
  }
  else
  {
    digitalWrite(enablePinX, HIGH);
  }
  if (y == true)
  {
    digitalWrite(enablePinY, LOW);
  }
  else
  {
    digitalWrite(enablePinY, HIGH);
  }
}

void xClockwise(bool foo)
{
  if (foo == true)
  {
    digitalWrite(dirPinX, HIGH);
  }
  else
  {
    digitalWrite(dirPinX, LOW);
  }
}

void yClockwise(bool foo)
{
  if (foo == true)
  {
    digitalWrite(dirPinY, LOW);
  }
  else
  {
    digitalWrite(dirPinY, HIGH);
  }
}

void spin_continuous(float speedX = 10, float speedY = 10, int finalDelay = 100)
{
  bool xClock;
  bool yClock;

  if (speedX >= 0)
  {
    xClock = true;
  }
  else
  {
    xClock = false;
  }
  if (speedY >= 0)
  {
    yClock = true;
  }
  else
  {
    yClock = false;
  }

  long IntervalX = (6e7 / speedX) / nStepsPerRotX;
  long IntervalY = (6e7 / speedY) / nStepsPerRotY;
  unsigned long stepsY = 0;
  unsigned long stepsX = 0;
  unsigned long previousTimeX = micros();
  unsigned long previousTimeY = micros();

  while (true)
  {
    unsigned long currentTimeX = micros();
    unsigned long currentTimeY = micros();
    bool xGo = false; // whether to step x
    bool yGo = false; // whether to step y
    bool skipCompensation = false;

    digitalWrite(stepPinX, HIGH);
    digitalWrite(stepPinY, HIGH);

    if (currentTimeX - previousTimeX > IntervalX)
    {
      xGo = true;
    }
    if (currentTimeY - previousTimeY > IntervalY)
    {
      yGo = true;
    }
    if (yGo == true && xGo == true && yClock == false && xClock != yClock)
    {
      skipCompensation = true;
    }

    if (xGo)
    {
      xClockwise(xClock);
      digitalWrite(stepPinX, LOW);
      digitalWrite(stepPinX, HIGH);
      previousTimeX = currentTimeX;

      if (skipCompensation == false)
      {
        yClockwise(!xClock); // spin y motor with x

        digitalWrite(stepPinY, LOW); // compensator
        digitalWrite(stepPinY, HIGH);
      }
      stepsX++;
    }

    if (yGo)
    {
      yClockwise(yClock);
      digitalWrite(stepPinY, LOW);
      digitalWrite(stepPinY, HIGH);
      previousTimeY = currentTimeY;
      stepsY++;
    }
    //    if (stepsX >= nStepsX && stepsY >= nStepsY) {keepGoing = false;} // check if finished
  }
  delay(finalDelay);
}

void spin_degs(float degX, float degY, float speedX = 10, float speedY = 10, int finalDelay = 100)
{
  // This function is perfect without accel
  // Initialize motor direction based on target degrees
  bool xClock = (degX >= 0);
  bool yClock = (degY >= 0);

  // Calculate steps needed for each axis based on degree input
  int nStepsX = nStepsPerRotX * abs(degX / 360.0);
  int nStepsY = nStepsPerRotY * abs(static_cast<float>(degY) / 360.0);

  // Determine intervals for each motor based on speed
  long intervalX = (6e7 / speedX) / nStepsPerRotX;
  long intervalY = (6e7 / speedY) / nStepsPerRotY;

  // Initialize step counters and timing variables
  unsigned long stepsX = 0;
  unsigned long stepsY = 0;
  unsigned long previousTimeX = micros();
  unsigned long previousTimeY = micros();

  while (stepsX < nStepsX || stepsY < nStepsY)
  {
    unsigned long currentTime = micros();
    bool skipCompensation = false;

    // Check if it's time to move motor X
    if ((currentTime - previousTimeX > intervalX) && (stepsX < nStepsX))
    {
      // Move X motor
      xClockwise(xClock);
      digitalWrite(stepPinX, LOW);
      digitalWrite(stepPinX, HIGH);
      previousTimeX = currentTime;
      stepsX++;

      // Compensation logic: Skip compensation when both axes move, Y motor moves in opposite direction to X
      if (!(stepsY < nStepsY && (currentTime - previousTimeY > intervalY) && yClock != xClock))
      {
        // Move Y motor to compensate
        yClockwise(!xClock);
        digitalWrite(stepPinY, LOW);
        digitalWrite(stepPinY, HIGH);
      }
    }

    // Check if it's time to move motor Y
    if ((currentTime - previousTimeY > intervalY) && (stepsY < nStepsY))
    {
      // Move Y motor
      yClockwise(yClock);
      digitalWrite(stepPinY, LOW);
      digitalWrite(stepPinY, HIGH);
      previousTimeY = currentTime;
      stepsY++;
    }
  }

  delay(finalDelay); // Final delay to settle motors
}

void RPM()
{
  spin_degs(random(-360, 360), random(-360, 360));
}

// Unit tests

void calibrate_pulley_teeth()
{
  spin_degs(90.0, 0);
  spin_degs(-90.0, 0);
  spin_degs(0, 90.0);
  spin_degs(0, -90.0);
}

void test_spin_degs_multi()
{
  spin_degs(90, -90);
  spin_degs(-90, 90);
  spin_degs(180, -180);
  spin_degs(-180, 180);
  spin_degs(360, 360);
  spin_degs(-360, -360);
}

void setup()
{
  pinMode(buttonPin, INPUT);
  pinMode(LED_BUILTIN, OUTPUT);
  pinMode(stepPinX, OUTPUT);
  pinMode(dirPinX, OUTPUT);
  pinMode(stepPinY, OUTPUT);
  pinMode(dirPinY, OUTPUT);
  pinMode(enablePinX, OUTPUT);
  pinMode(enablePinY, OUTPUT);
  Serial.begin(9600);
  Serial.print("--\nHello from OpenClino.\n--");
  wake(false, false);
}

void loop()
{
  buttonState = digitalRead(buttonPin);

  // Turn off motors when button is not pressed.
  wake(false, false);

  if (buttonState == HIGH)
  {
    digitalWrite(LED_BUILTIN, HIGH);
    wake(true, true);
    calibrate_pulley_teeth();
    test_spin_degs_multi();
    // uncomment to run continuous spin
    // spin_continuous(4, 20);
    // uncomment to run RPM
    // RPM();
  }
}

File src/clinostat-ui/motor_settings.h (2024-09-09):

#ifndef MOTOR_SETTINGS_H
#define MOTOR_SETTINGS_H

// Your motor settings

// should match your motor specs
const int motorSteps = 200;
// should match your controller
const int subStep = 32;
const int stepsPerRevolution = motorSteps * subStep;

// should match clinostate build

// dimater of X motor pulley
const float xMotD = 12.0;
const float xPulleyD = 31.5;
const float yMotD = 12.0;
const float yTurnD = 31.5;
const float yPulleyD = 18.5;
const float xRatio = xPulleyD/xMotD; // diameters
const float yRatio = yPulleyD/yMotD;

const int X_MOTOR = 0;
const int Y_MOTOR = 1;
const int NO_MOTORS = 2;

#endif

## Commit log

2023-12-27 3MF files uploaded
    [m2y v5.3mf, m_base v7.3mf, m_enclosure v2.3mf, x_body v9.3mf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]
2024-03-16 new m_base! 🚧
    [m_base v9.3mf]
2024-11-29 #2 Calibrate pulley teeth (#9)
    * restructure openclino
    * Setup 2.0 dev and object
    * classes functional
    * testing AccelStepper
    * test accelStepper, unit test spin_degs
    * spin_degs calibrated, spin_continuous broken
    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
2025-03-15 0.3.1 (#18)
    * 0.3.0
    * update docs
    * fix build guide
    * fix admonitions
    * check NULL in calibration
2025-06-02 Fix calibration return and add comments (#21)
2025-12-26 rm y_pulley 3mf
    [y_pulley v3.3mf]
2025-12-31 Vesion 0.5.0 - Partial gravity (#26)
    # Version 0.5.0 31/12/2025
    ## Major Partial Gravity Simulation Update
    - Restructure to modular code `openclino.h` (header file), `openclino.cpp` (code), and `openclino.ino` (arduino).
    - MicroSD card.
    - Add MicroSD card reader to optional circuit design image.
    - Add MicroSD card debugging scripts `test_sd` and `test_path`.
    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
2026-03-21 Update CHANGELOG for version 0.5.2
    Updated version number to 0.5.2 and added a new entry for version 0.5.1 with a fix for the circuit image path.
